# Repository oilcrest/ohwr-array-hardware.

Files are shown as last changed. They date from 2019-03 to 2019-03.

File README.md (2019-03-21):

# Overview

Hardware of the ARRAY system for silicon sensor testing consisting of two Printed Circuit Boards:
* an active 512-to-1 switching matrix,
* a passive probe card to contact the sensor.

# Copyright

Copyright CERN 2013.
This documentation describes Open Hardware and is licensed under the CERN OHL v. 1.2.

You may redistribute and modify this documentation under the terms of the CERN OHL v.1.2. (http://ohwr.org/cernohl). This documentation is distributed WITHOUT ANY EXPRESS OR IMPLIED WARRANTY, INCLUDING OF MERCHANTABILITY, SATISFACTORY QUALITY AND FITNESS FOR A PARTICULAR PURPOSE. Please see the CERN OHL v.1.2 for applicable conditions.

# PCB design files

* [Switching matrix design](/Switching_Matrix)
* [Probe card design](/Probe_Card)

# PCB images

Switching matrix

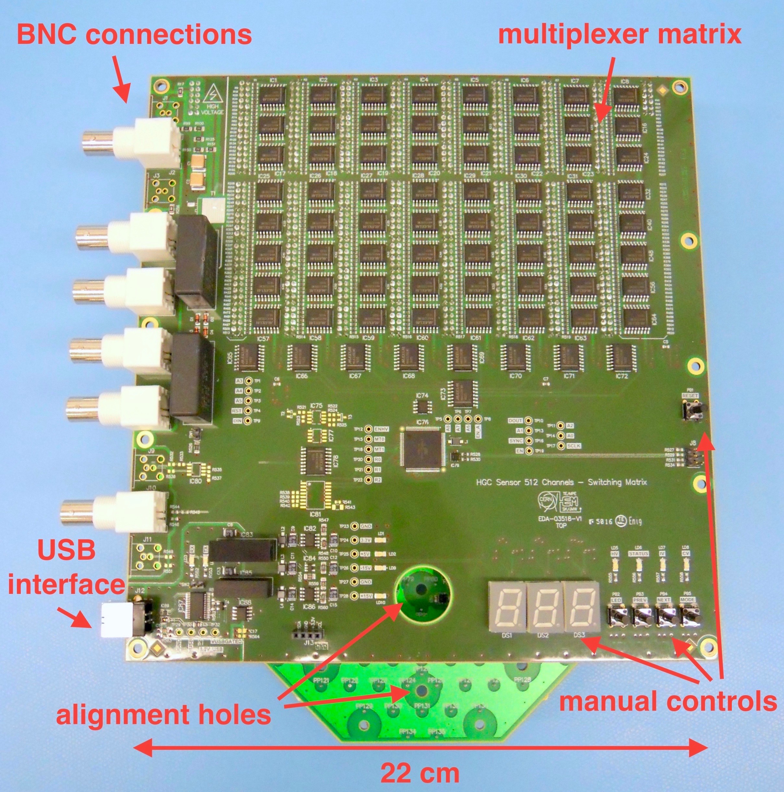
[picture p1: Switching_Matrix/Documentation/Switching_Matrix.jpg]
SwitchingMatrix


Probe card

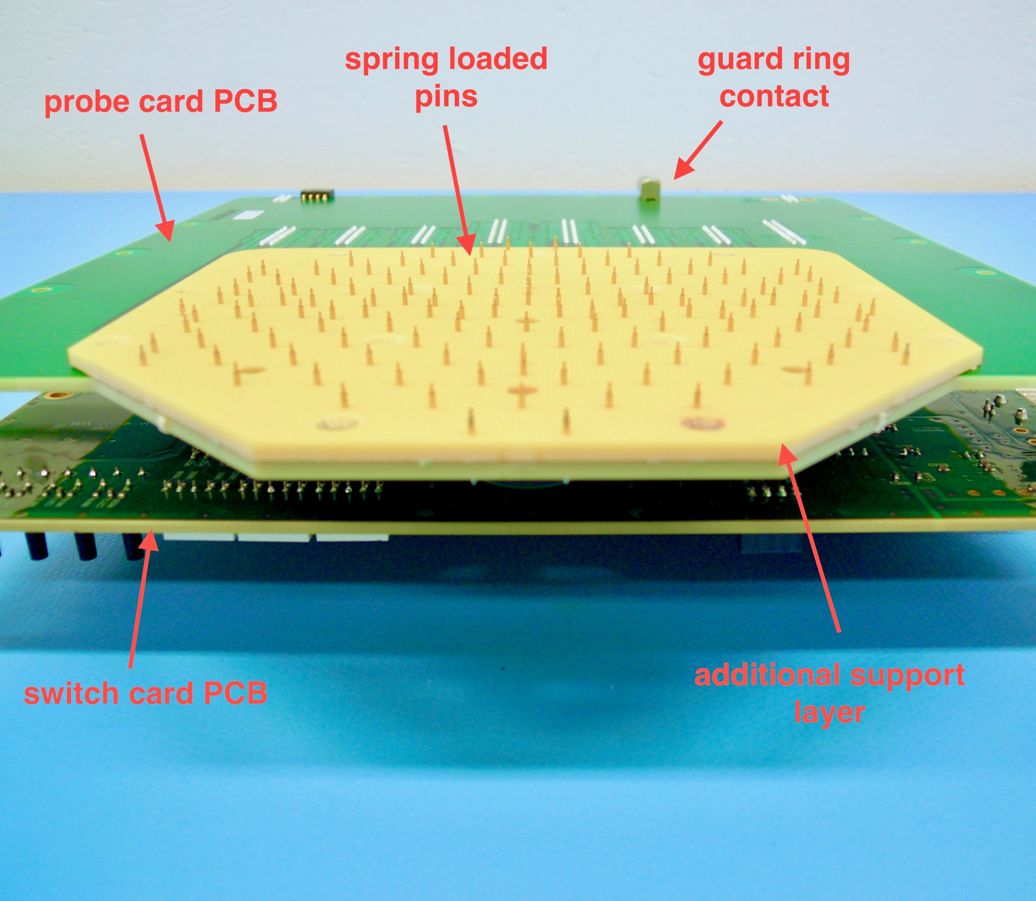
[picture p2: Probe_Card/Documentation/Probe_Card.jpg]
ProbeCard


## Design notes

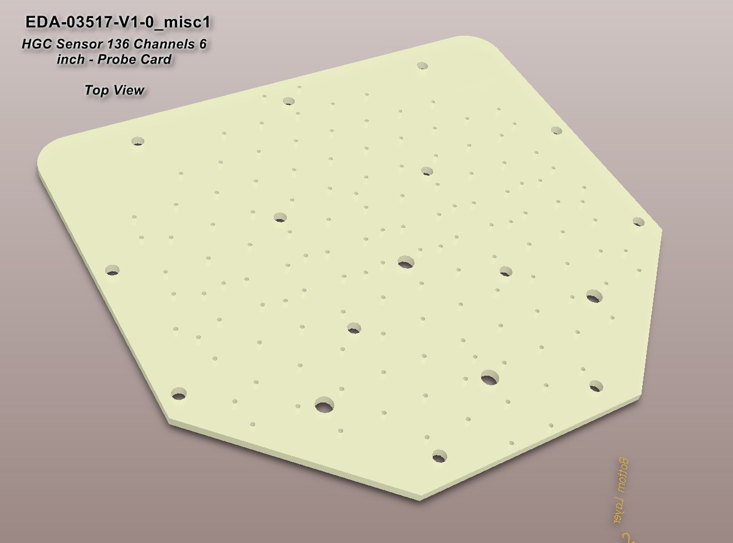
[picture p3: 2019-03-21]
Probe_Card/Picture/EDA-03517-V1-0_3D_misc1-top.jpg

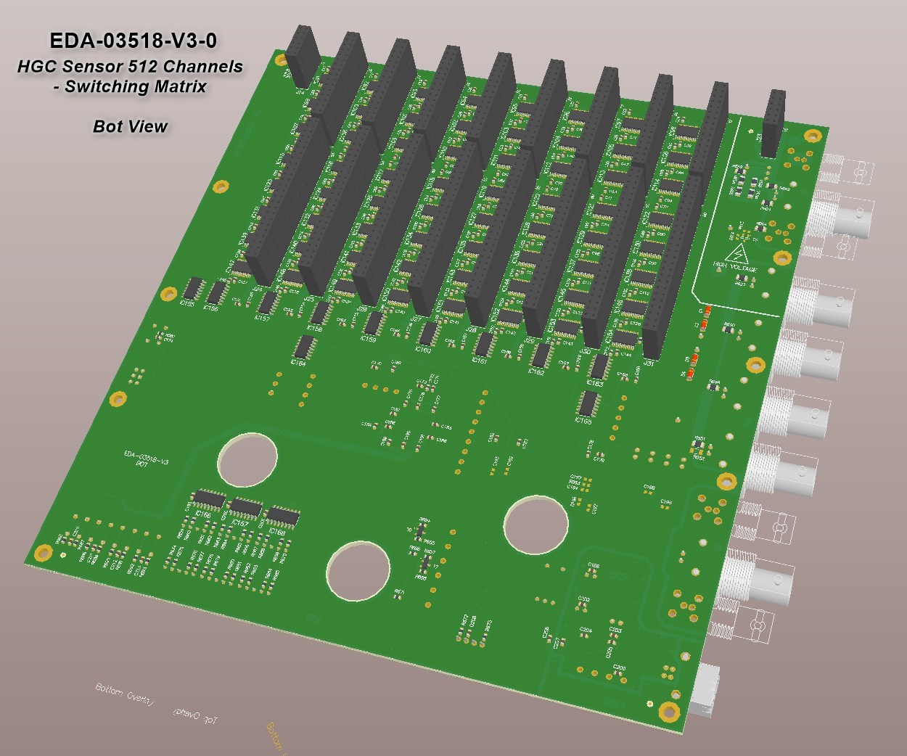
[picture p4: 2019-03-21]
Switching_Matrix/Picture/EDA-03518-V3-0_3D-bot.jpg

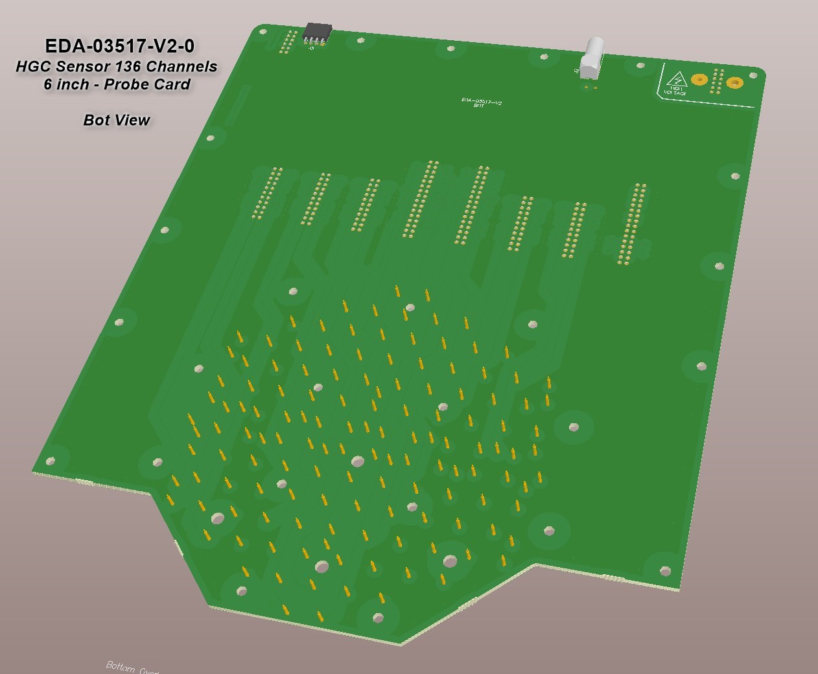
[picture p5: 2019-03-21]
Probe_Card/Picture/EDA-03517-V2-0_3D-bot.jpg

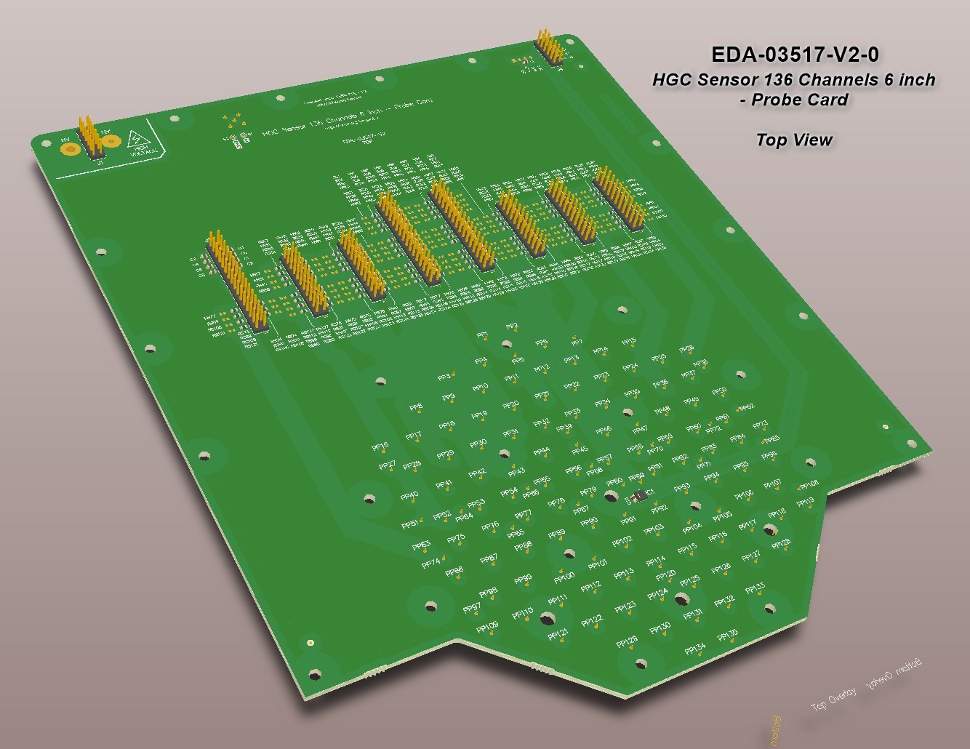
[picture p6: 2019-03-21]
Probe_Card/Picture/EDA-03517-V2-0_3D-top.jpg

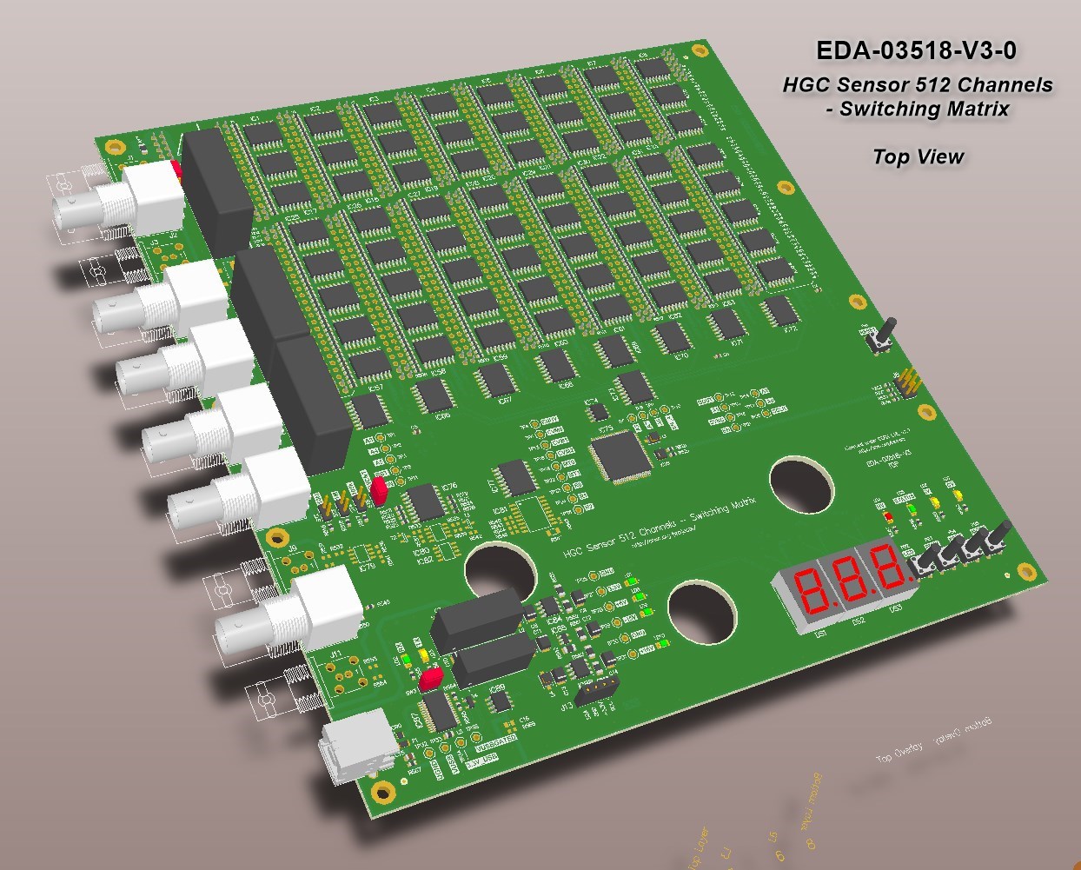
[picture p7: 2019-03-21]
Switching_Matrix/Picture/EDA-03518-V3-0_3D-top.jpg

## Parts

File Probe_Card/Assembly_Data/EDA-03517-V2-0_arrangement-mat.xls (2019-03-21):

 |  | Project | -
 |  | Title | HGC Sensor 136 Channels 6 inch - Probe Card
 |  | EDA Number | EDA-03517-V2-0 | Rev.
 |  | Designer | E. Sicking | Drawn by | JMW
 |  | File | EDA-03517-V2-0_arrangement-mat.xls | EDMS Link | https://edms.cern.ch/nav/EDA-03517-V2-0 | https://edms.cern.ch/nav/EDA-03517-V2-0
 |  | Date | 2019-02-12
Ref | Qty | Scem | Description | Val&Device | Manufacturer | Part Number | Observations
PCBs
1 | 1 |  | "HGC Sensor 136 Channels 6 inch - Probe Card" Printed Circuit | EDA-03517-V2-0 (https://edms.cern.ch/nav/EDA-03517-V2-0) |  |  | EDA-03517-V2-0_pcb
2 | 1 |  | "HGC Sensor 136 Channels 6 inch - Probe Card_misc1" Printed Circuit | https://edms.cern.ch/nav/EDA-03517-V2-0 |  |  | EDA-03517-V1-0_misc1
Screws
10 | 13 |  | Hexalobular (6 Lobe) Socket Flat Head Countersunk Screw, Fully Threaded, ISO 14581, Stainless Steel A2 | M3 - L=8mm | BOSSARD | BN 3803 Article No. 3061684
11 | 13 |  | Waved Spring Washer, DIN 137 B, Spring Steel 440-520 HV, Zinc Plated Blue | fit for M3 | BOSSARD | BN 83728 Article No. 8243964
12 | 13 |  | Hexagonal Nut ~0.8D, DIN 934, Stainless Steel A2 | M3 | BOSSARD | BN 628 Article No. 1241443

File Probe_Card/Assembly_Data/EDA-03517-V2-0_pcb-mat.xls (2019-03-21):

 |  | Project | -
 |  | Title | HGC Sensor 136 Channels 6 inch Probe Card
 |  | EDA Number | EDA-03517-V2-0 | Rev.
 |  | Designer | E. Sicking | Drawn by | JMW
 |  | File | EDA-03517-V2-0_pcb-mat.xls | EDMS URL | https://edms.cern.ch/item/EDA-03517-V2-0
 |  | Date | 2019-02-20
Ref | Qty | Scem | Description | Val&Device | Manufacturer | Part Number | Case
C1 | 2 |  | ±10% 50V X7R SMD Multilayer Chip Ceramic Capacitor | 100nF | GENERIC | CC0603_100NF_50V_10%_X7R | 0603
C10
C2 | 1 |  | ±0.25pF 50V C0G/NP0 SMD Multilayer Chip Ceramic Capacitor | 1pF | GENERIC | CC0603_1PF_50V_0.25PF_NP0 | 0603
C3 | 1 |  | ±0.25pF 50V C0G/NP0 SMD Multilayer Chip Ceramic Capacitor | 2.2pF | GENERIC | CC0603_2.2PF_50V_0.25PF_NP0 | 0603
C4 | 1 |  | ±0.25pF 50V C0G/NP0 SMD Multilayer Chip Ceramic Capacitor | 4.7pF | GENERIC | CC0603_4.7PF_50V_0.25PF_NP0 | 0603
C5 | 1 |  | ±5% 50V C0G/NP0 SMD Multilayer Chip Ceramic Capacitor | 10pF | GENERIC | CC0603_10PF_50V_5%_NP0 | 0603
C6 | 1 |  | ±5% 50V C0G/NP0 SMD Multilayer Chip Ceramic Capacitor | 22pF | GENERIC | CC0603_22PF_50V_5%_NP0 | 0603
C7 | 1 |  | ±5% 50V C0G/NP0 SMD Multilayer Chip Ceramic Capacitor | 47pF | GENERIC | CC0603_47PF_50V_5%_NP0 | 0603
C8 | 1 |  | ±5% 50V C0G/NP0 SMD Multilayer Chip Ceramic Capacitor | 100pF | GENERIC | CC0603_100PF_50V_5%_NP0 | 0603
C9 | 1 |  | ±5% 50V C0G/NP0 SMD Multilayer Chip Ceramic Capacitor | 220pF | GENERIC | CC0603_220PF_50V_5%_NP0 | 0603
J1 | 2 |  | 12 Contacts, Pitch 2.54mm, Dual Row Through Mount Straight Header |  | SAMTEC | MTLW-106-07-L-D-250
J4 |  |  | (Post Lead = 6.35mm, Tail Lead 3.05mm, Insulator 1.52mm)
J2 | 1 | 09.46.11.180.6 (https://edh.cern.ch/edhcat/Browser?command=searchItems&scem=09.46.11.180.6) | Size 00, 50 Ohms Coaxial Elbow (90°) socket With Clearance Under The Body |  | LEMO | EPK.00.250.NTN
J3 | 1 |  | 4 Contacts, Pitch 2.54mm, Single Row Through Mount Right Angle Socket (Lead Length 2.54mm) |  | SAMTEC | SSW-104-02-L-S-RA
J5 | 3 |  | 32 Contacts, Pitch 2.54mm, Dual Row Through Mount Straight Header |  | SAMTEC | MTLW-116-07-L-D-250
J8, J9 |  |  | (Post Lead = 6.35mm, Tail Lead 3.05mm, Insulator 1.52mm)
J6, J7 | 5 |  | 22 Contacts, Pitch 2.54mm, Dual Row Through Mount Straight Header |  | SAMTEC | MTLW-111-07-L-D-250
J10 > J12 |  |  | (Post Lead = 6.35mm, Tail Lead 3.05mm, Insulator 1.52mm)
PP1 > PP135 | 135 |  | Probe, Spring-Loaded Pin, 2A Continuous, 3A Peak, -55..125°C (Soldered Pin 3.81mm) |  | MILL-MAX | 0985-1-15-20-71-14-11-0
RS1 > RS135 | 135 |  | 1A (0.05R Max DC Resistance) Zero Ohm Jumper | 0 | GENERIC | R0603_0R_JUMPER | 0603
Sensitive
IC1 | 1 |  | I2C Digital Humidity 0 – 100% RH and Temperature -40°C to +125°C Sensor | SHT25 | SENSIRION | SHT25 | SON6
Not Mounted
R1 > R4 | 4 |  | ±1% 0.1W ±100ppm/°C General Purpose Thick Film Chip Resistor | 10k | GENERIC | R0603_10K_1%_0.1W_100PPM | 0603
RB1 > RB135 | 135 |  | ±1% 0.125W ±100ppm/°C High Stability Metal Glaze Thick Film Chip Resistor | 10M | VISHAY SFERNICE | CHP0603K1005FNT | 0603
 | Dimensions: |  | Through Pins | 427
 | 220 x 264mm |  | SMD pins on Top | 297
 |  |  | SMD pins on Bottom | 0
 |  |  | Total number of pins | 724

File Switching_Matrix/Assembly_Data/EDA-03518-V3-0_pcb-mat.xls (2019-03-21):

 |  | Project | HGC Sensor Probe Card
 |  | Title | HGC Sensor 512 Channels - Switching Matrix
 |  | EDA Number | EDA-03518-V3-0 | Rev.
 |  | Designer | Szymon Kulis | Drawn by | JMW
 |  | File | EDA-03518-V3-0_pcb-mat.xls | EDMS URL | https://edms.cern.ch/item/EDA-03518-V3-0
 |  | Date | 2019-02-21
Ref | Qty | Scem | Description | Val&Device | Manufacturer | Part Number | Case
C1 > C3 | 3 |  | ±5% 1200VDC Metallized Polypropylene Film Capacitor (MKP1848C DC-Link) | 1uF | VISHAY ROEDERSTEIN | MKP1848C51012JK2 | LS27.5 W11 x L32 x H21
C4 > C6 | 188 |  | ±10% 50V X7R SMD Multilayer Chip Ceramic Capacitor | 100nF | GENERIC | CC0603_100NF_50V_10%_X7R | 0603
C17 > C171
C173 > C186
C189 > C191
C199 > C201
C203 > C208
C210 > C213
C7 > C14 | 8 |  | ±10% 20V Low ESR 0R4 Solid Tantalum Chip Capacitor | 22uF | GENERIC | CTE3528-21_22UF_20V_10%_LESR0400 | B
C15 | 1 |  | ±10% 250V X7R SMD Multilayer Chip Ceramic Capacitor | 4.7nF | GENERIC | CC0805_4.7NF_250V_10%_X7R | 0805
C172 | 1 |  | ±20% 16V X5R SMD Multilayer Chip Ceramic Capacitor | 10uF | GENERIC | CC0603_10UF_16V_20%_X5R | 0603
C198 | 3 |  | ±10% 50V X7R SMD Multilayer Chip Ceramic Capacitor | 10nF | GENERIC | CC0603_10NF_50V_10%_X7R | 0603
C202
C209
D1 > D4 | 4 |  | 10V 500mW Voltage Regulator Diode | BZV55-B10 | NEXPERIA | BZV55-B10 | SOD-80C
DS1 > DS3 | 3 |  | 13.2mm Single Digit 7-Segment Red Display, Common Anode, Right Hand Dot Point | SA52-11SRWA | KINGBRIGHT | SA52-11SRWA
F1 | 1 |  | PTC Resettable Fuse | 500mA-6V | BOURNS | MF-PSMF050X-2
IC1 > IC73 | 75 |  | Ultra-Low Leakage Monolithic CMOS Analog Multiplexers | MAX328EWE+ | MAXIM | MAX328EWE+ | SOIC16W
IC76, IC77
IC74 | 1 |  | 2.048V Output, ±1mV ±0.05% Accuracy, 3ppm/°C Ultralow Noise XFET Voltage References with Current Sink and Source Capability | ADR440BRZ | ANALOG DEVICES | ADR440BRZ | SOIC8
IC75 | 1 |  | 8/16-bit AVR XMEGA A1U Microcontroller, 1.6-3.6V, 128KB + 8KB Flash, 2KB EEPROM, 8KB SRAM, 100-pin TQFP, Industrial Grade (-40°C to 85°C), Pb-Free | ATXMEGA128A1U-AU | ATMEL | ATXMEGA128A1U-AU | QFP100
IC83 | 1 |  | 5V ±10% to 5V, Iout (max) 200mA, 1W DC-DC Converter | TMV 0505EN | TRACO POWER | TMV 0505EN
IC84 | 2 |  | 20V, 500mA, Low Noise, CMOS LDO Linear Regulator | ADP7104ARDZ-R7 | ANALOG DEVICES | ADP7104ARDZ-R7 | SOIC8
IC88
IC85 | 1 |  | -1.22V to -27V, -200mA, Adjustable, Low Noise, Negative Linear Regulator | ADP7182AUJZ-R7 | ANALOG DEVICES | ADP7182AUJZ-R7 | SOT23-5
IC86 | 1 |  | 5V ±10% to ±15V, Iout (max) ±65mA, 1W DC-DC Converter | TMV 0515D | TRACO POWER | TMV 0515D
IC87 | 1 |  | USB to serial UART Interface | FT232RL | FUTURE TECHNOLOGYDEVICES INTERNATIONAL (FTDI) | FT232RL | SSOP28
IC89 | 1 |  | Dual Channel Digital Isolator | ISO7221AD | TEXAS INSTRUMENTS | ISO7221AD | SOIC8
IC90 | 1 |  | 2 Data-Line Protection, Very Low Capacitance ESD Protection | USBLC6-2P6 | ST MICROELECTRONICS | USBLC6-2P6 | SOT666
IC91 > IC154 | 64 |  | 9.5 Ohm ON Resistance, ±15 V/+12 V/±5 V iCMOS, Serially-Controlled Octal SPST Switches | ADG1414BRUZ | ANALOG DEVICES | ADG1414BRUZ | TSSOP24
IC155 > IC165 | 11 |  | Hex Inverters | 74HC04D | NXP SEMICONDUCTORS | 74HC04D | SOIC14
IC166 > IC168 | 3 |  | 8-Bit Shift Register With 3-State Output Registers | SN74HC595D | TEXAS INSTRUMENTS | SN74HC595D | SOIC16
J2 | 6 |  | 50 Ohms BNC Elbow PCB Socket With Mounting Posts |  | TYCO ELECTRONICS | 1-1337543-0
J4 > J7
J10
J8 | 1 |  | 6 Contacts, Pitch 2.54mm, Dual Row Through Mount Straight Header (Post Lead = 6.35mm, Tail Lead 3.05mm, Insulator 1.52mm) |  | SAMTEC | MTLW-103-07-L-D-250
J12 | 1 |  | Thru Hole, Right Angle, 4 Position, Type B, USB Receptacle |  | TYCO ELECTRONICS | 292304-1
J13 | 1 |  | 4 Contacts, Pitch 2.54mm, Single Row Through Mount Straight Socket (Lead Length 4.93mm) |  | SAMTEC | SSW-104-02-L-S
J14 | 2 |  | 12 Contacts, Pitch 2.54mm, Dual Row Through Mount Straight Elevated Socket, |  | SAMTEC | ESW-106-69-L-D
J23 |  |  | Low Insertion Force (Lead Length 4.57mm)
J15 > J22 | 8 |  | 32 Contacts, Pitch 2.54mm, Dual Row Through Mount Straight Elevated Socket, Low Insertion Force (Lead Length 4.57mm) |  | SAMTEC | ESW-116-69-L-D
J24 > J31 | 8 |  | 50 Contacts, Pitch 2.54mm, Dual Row Through Mount Straight Elevated Socket, Low Insertion Force (Lead Length 4.57mm) |  | SAMTEC | ESW-125-69-L-D
L1 | 1 |  | ±10% 450mA Chip Inductor (Chip Coil) for Choke Wire Wound Type | 10uH | MURATA | LQH32CN100K33L
L2 > L4 | 3 |  | ±20% 650mA Chip Inductor (Chip Coil) for Choke Wire Wound Type | 4.7uH | MURATA | LQH32CN4R7M33L
L5 | 1 |  | ±25% 2A SMD EMI Suppression Chip Ferrite Bead (WE-CBF Series) | 330R@100MHz | WURTH ELEKTRONIK | 742792037 | 0805
LD1, LD2 | 6 |  | Surface Mount Green LED (1206 Case) |  | AVAGO TECHNOLOGIES | HSMG-C150 | 1206
LD5
LD8 > LD10
LD3 | 3 |  | Yellow Diffused Surface Mount LED (1206 Case) |  | AVAGO TECHNOLOGIES | HSMY-C150 | 1206
LD6, LD7
LD4 | 1 |  | Surface Mount Red LED (1206 Case) |  | AVAGO TECHNOLOGIES | HSMC-C150 | 1206
R1 > R16 | 525 |  | ±1% 0.1W ±100ppm/°C General Purpose Thick Film Chip Resistor | 10k | GENERIC | R0603_10K_1%_0.1W_100PPM | 0603
R18 > R249
R251 > R514
R526
R529
R569, R570
R579, R580
R650
R672, R673
R686
R688
R690
R692
R17 | 10 |  | 2A (0.05R Max DC Resistance) Zero Ohm Jumper | 0 | GENERIC | R1206_0R_JUMPER | 1206
R250
R589
R592
R603, R604
R623
R640
R649
R651
R515 | 2 |  | ±1% 0.1W ±100ppm/°C General Purpose Thick Film Chip Resistor | 10M | GENERIC | R0603_10M_1%_0.1W_100PPM | 0603
R521
R516 | 2 |  | ±1% 0.1W ±100ppm/°C General Purpose Thick Film Chip Resistor | 1M | GENERIC | R0603_1M_1%_0.1W_100PPM | 0603
R522
R517, R518 | 9 |  | ±1% 0.1W ±100ppm/°C General Purpose Thick Film Chip Resistor | 100k | GENERIC | R0603_100K_1%_0.1W_100PPM | 0603
R565
R654
R657
R687
R689
R691
R693
R519 | 1 |  | ±1% 0.1W ±100ppm/°C High-Value High-voltage (150V) Wraparound Chip Resistor | 5M | OHMITE | HVC0603T5004FET | 0603
R520 | 1 |  | ±1% 0.1W ±100ppm/°C General Purpose Thick Film Chip Resistor | 510k | GENERIC | R0603_510K_1%_0.1W_100PPM | 0603
R523 | 6 |  | 1A (0.05R Max DC Resistance) Zero Ohm Jumper | 0 | GENERIC | R0603_0R_JUMPER | 0603
R527
R530
R534
R548
R550
R524 | 1 |  | ±5% 0.1W ±100ppm/°C High-Value High-voltage (150V) Wraparound Chip Resistor | 50M | OHMITE | HVC0603T5005FET | 0603
R525 | 1 |  | ±1% 0.1W ±100ppm/°C General Purpose Thick Film Chip Resistor | 2M | GENERIC | R0603_2M_1%_0.1W_100PPM | 0603
R528 | 1 |  | ±1% 0.1W ±100ppm/°C Precision High-Value High-Voltage Wraparound Chip Resistor | 100M | OHMITE | HVC0603T1006FET | 0603
R549 | 1 |  | ±1% 0.1W ±100ppm/°C General Purpose Thick Film Chip Resistor | 51 | GENERIC | R0603_51R_1%_0.1W_100PPM | 0603
R551 | 1 |  | ±1% 0.25W ±100ppm/°C General Purpose Thick Film Chip Resistor | 36k | GENERIC | R1206_36K_1%_0.25W_100PPM | 1206
R552 | 1 |  | ±1% 0.25W ±100ppm/°C General Purpose Thick Film Chip Resistor | 62k | GENERIC | R1206_62K_1%_0.25W_100PPM | 1206
R555, R556 | 2 |  | ±1% 0.1W ±100ppm/°C General Purpose Thick Film Chip Resistor | 220 | GENERIC | R0603_220R_1%_0.1W_100PPM | 0603
R557 > R560 | 5 |  | ±1% 0.1W ±100ppm/°C General Purpose Thick Film Chip Resistor | 330 | GENERIC | R0603_330R_1%_0.1W_100PPM | 0603
R655
R561 | 2 |  | ±1% 0.25W ±100ppm/°C General Purpose Thick Film Chip Resistor | 91k | GENERIC | R1206_91K_1%_0.25W_100PPM | 1206
R566
R562, R563 | 2 |  | ±1% 0.25W ±100ppm/°C General Purpose Thick Film Chip Resistor | 8k2 | GENERIC | R1206_8K2_1%_0.25W_100PPM | 1206
R564 | 1 |  | ±1% 0.1W ±100ppm/°C General Purpose Thick Film Chip Resistor | 1k | GENERIC | R0603_1K_1%_0.1W_100PPM | 0603
R567 | 1 |  | ±1% 0.1W ±100ppm/°C General Purpose Thick Film Chip Resistor | 1M1 | GENERIC | R0603_1M1_1%_0.1W_100PPM | 0603
R571 > R578 | 64 |  | ±1% 0.1W ±100ppm/°C General Purpose Thick Film Chip Resistor | 33k | GENERIC | R0603_33K_1%_0.1W_100PPM | 0603
R581 > R588
R595 > R602
R605 > R612
R615 > R622
R624 > R639
R641 > R648
R590, R591 | 4 |  | ±1% 0.25W ±100ppm/°C General Purpose Thick Film Chip Resistor | 10k | GENERIC | R1206_10K_1%_0.25W_100PPM | 1206
R593, R594
R656 | 1 |  | ±1% 0.1W ±100ppm/°C General Purpose Thick Film Chip Resistor | 750 | GENERIC | R0603_750R_1%_0.1W_100PPM | 0603
R658 | 2 |  | ±1% 0.1W ±100ppm/°C General Purpose Thick Film Chip Resistor | 2k4 | GENERIC | R0603_2K4_1%_0.1W_100PPM | 0603
R671
R659 > R670 | 24 |  | ±1% 0.1W ±100ppm/°C General Purpose Thick Film Chip Resistor | 3k3 | GENERIC | R0603_3K3_1%_0.1W_100PPM | 0603
R674 > R685
ST1 | 1 |  | 3 Contacts, Pitch 2.54mm, Single Row Through Mount Straight Header (Post Lead = 6.35mm, Tail Lead 3.05mm, Insulator 1.52mm) |  | SAMTEC | MTLW-103-07-L-S-250
ST2 > ST6 | 5 |  | 2 Contacts, Pitch 2.54mm, Single Row Through Mount Straight Header (Post Lead = 6.35mm, Tail Lead 3.05mm, Insulator 1.52mm) |  | SAMTEC | MTLW-102-07-L-S-250
SW1 > SW3 | 3 | 09.55.10.950.1 (https://edh.cern.ch/edhcat/Browser?command=searchItems&scem=09.55.10.950.1) | Closed Insulated Red Jumper Pitch 2.54mm |  | STELVIO-KONTEK | 3131730000402
T4 | 1 |  | -20V -3.7A P-Channel HEXFET® Power MOSFET | IRLML6402PBF | INTERNATIONAL RECTIFIER | IRLML6402PBF | SOT23-3
T6 | 1 |  | 60V 280mA N-Channel Enhancement Mode Field Effect Transistor (FET) | 2N7002 | FAIRCHILD SEMICONDUCTOR | 2N7002 | SOT23-3
T7 | 1 |  | -30V -470mA P-Channel Enhancement Mode MOS Transistor | BSH203 | NXP SEMICONDUCTORS | BSH203 | SOT23-3
Sensitive
IC78 | 1 |  | I2C Digital Humidity 0 – 100% RH and Temperature -40°C to +125°C Sensor | SHT25 | SENSIRION | SHT25 | SON6
PB1 > PB5 | 5 |  | 12VDC 50mA, 6x6mm Model, 13mm Stem Height Vertical Pushbutton Switch, ALPS SKHH Series |  | ALPS | SKHHDTA010
Not Mounted
C16 | 1 |  | ±10% 250V X7R SMD Multilayer Chip Ceramic Capacitor | 4.7nF | GENERIC | CC0805_4.7NF_250V_10%_X7R | 0805
C187, C188 | 8 |  | ±10% 50V X7R SMD Multilayer Chip Ceramic Capacitor | 100nF | GENERIC | CC0603_100NF_50V_10%_X7R | 0603
C192 > C197
IC79, IC80 | 2 |  | Dual Low-Noise JFET-Input Operational Amplifier | TL072CD | TEXAS INSTRUMENTS | TL072CD | SOIC8
IC81 | 1 |  | Ultra-Low Leakage Monolithic CMOS Analog Multiplexers | MAX328EWE+ | MAXIM | MAX328EWE+ | SOIC16W
IC82 | 1 |  | Low Power, Low Noise Precision FET Operational Amplifier | AD795JRZ | ANALOG DEVICES | AD795JRZ | SOIC8
J1 | 4 |  | TRB ( Twinax/Triax 500MHz) Right Angle PCB Jack |  | TROMPETER/CINCH | CBBJR79A
J3
J9
J11
R531 | 6 |  | 1A (0.05R Max DC Resistance) Zero Ohm Jumper | 0 | GENERIC | R0603_0R_JUMPER | 0603
R536
R538
R541
R553, R554
R532 | 1 |  | ±1% 0.1W ±100ppm/°C General Purpose Thick Film Chip Resistor | 470 | GENERIC | R0603_470R_1%_0.1W_100PPM | 0603
R533 | 2 |  | ±1% 0.1W ±100ppm/°C General Purpose Thick Film Chip Resistor | 100 | GENERIC | R0603_100R_1%_0.1W_100PPM | 0603
R535
R537 | 5 |  | ±1% 0.1W ±100ppm/°C General Purpose Thick Film Chip Resistor | 10k | GENERIC | R0603_10K_1%_0.1W_100PPM | 0603
R539, R540
R542
R653
R543 | 3 |  | ±1% 0.1W ±100ppm/°C General Purpose Thick Film Chip Resistor | 100k | GENERIC | R0603_100K_1%_0.1W_100PPM | 0603
R613, R614
R544 | 1 |  | ±1% 0.1W ±100ppm/°C General Purpose Thick Film Chip Resistor | 1M | GENERIC | R0603_1M_1%_0.1W_100PPM | 0603
R545 | 1 |  | ±1% 0.1W ±100ppm/°C Precision High-Value High-Voltage Wraparound Chip Resistor | 100M | OHMITE | HVC0603T1006FET | 0603
R546 | 1 |  | ±1% 0.1W ±100ppm/°C General Purpose Thick Film Chip Resistor | 10M | GENERIC | R0603_10M_1%_0.1W_100PPM | 0603
R547 | 1 |  | ±1% 0.3W ±100ppm/°C Thick Film Chip Resistor, High Voltage | 1G | VISHAY TECHNO | CRHV1206AF1G00FKFT | 1206
R568 | 1 |  | ±1% 0.1W ±100ppm/°C General Purpose Thick Film Chip Resistor | 1M1 | GENERIC | R0603_1M1_1%_0.1W_100PPM | 0603
R652 | 1 |  | 2A (0.05R Max DC Resistance) Zero Ohm Jumper | 0 | GENERIC | R1206_0R_JUMPER | 1206
T1 | 1 |  | 1500V 2A N-Channel Power MOSFET | 2SK4177-DL-1E | ON SEMICONDUCTOR | 2SK4177-DL-1E | TO-263-2L
T2, T3 | 3 |  | 60V 280mA N-Channel Enhancement Mode Field Effect Transistor (FET) | 2N7002 | FAIRCHILD SEMICONDUCTOR | 2N7002 | SOT23-3
T5
TP1 > TP35 | 35 |  | Black Bead PCB Terminal Test Pin for 1.6mm PCB Thickness (1.32mm Hole) |  | VERO TECHNOLOGIES | 20-2136
 | Dimensions: |  | Through Pins | 811
 | 220 x 230mm |  | SMD pins on Top | 2548
 |  |  | SMD pins on Bottom | 2372
 |  |  | Total number of pins | 5731

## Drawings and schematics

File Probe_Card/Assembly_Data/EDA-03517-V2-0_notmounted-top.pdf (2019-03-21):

J1 | J4

# 4 Not Mounted TOP

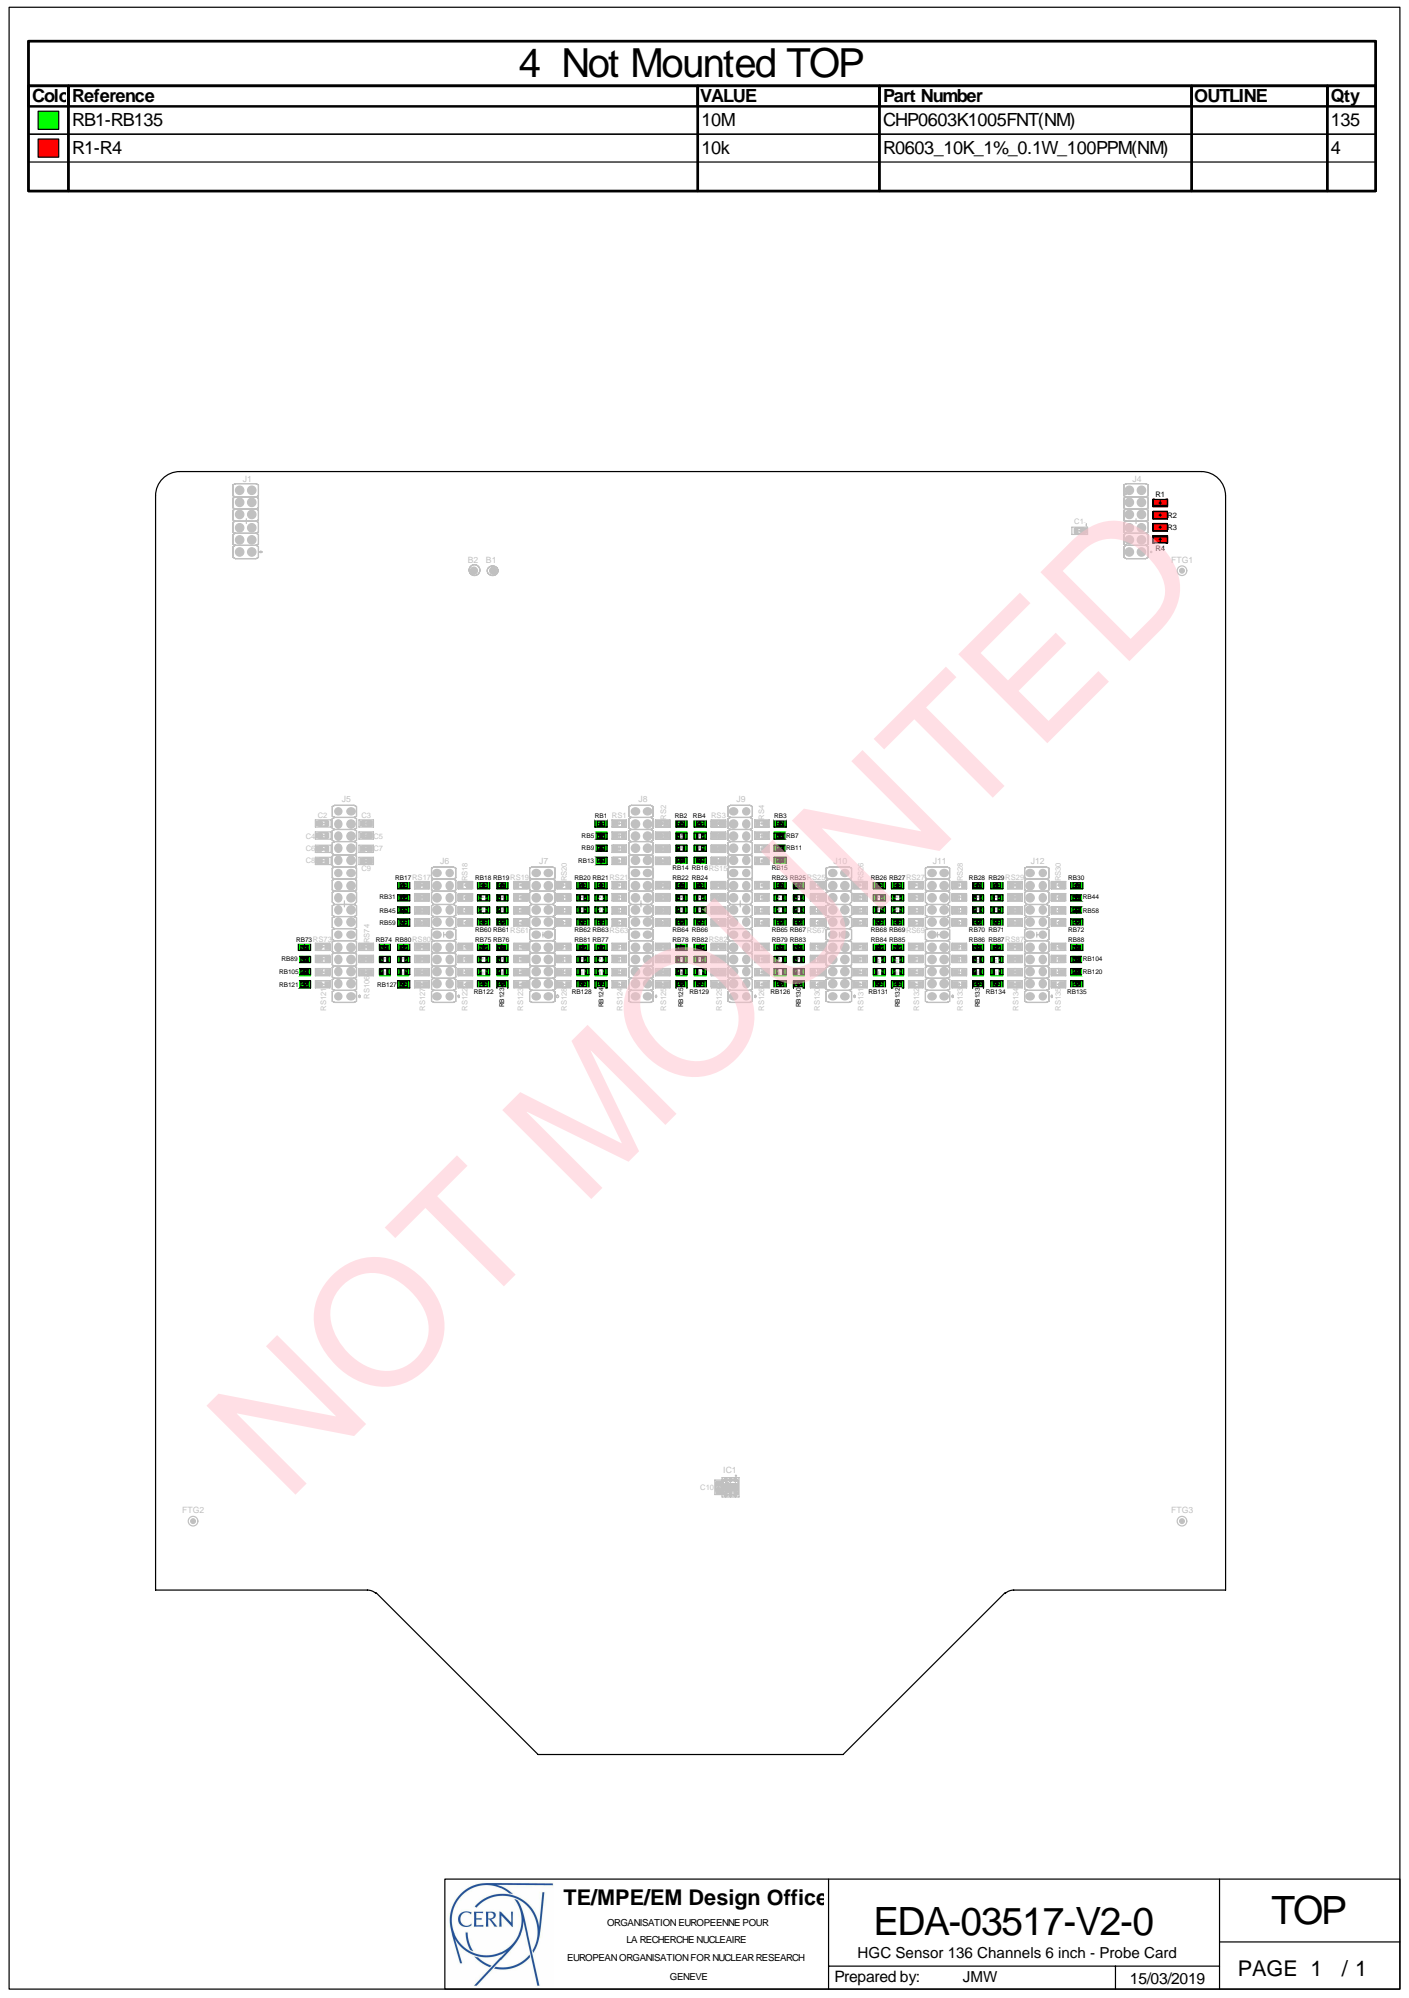
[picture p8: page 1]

TOP TE/MPE/EM Design Office

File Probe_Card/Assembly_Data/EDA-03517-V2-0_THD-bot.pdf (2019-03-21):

J3

# 3 Through-Holes BOTTOM

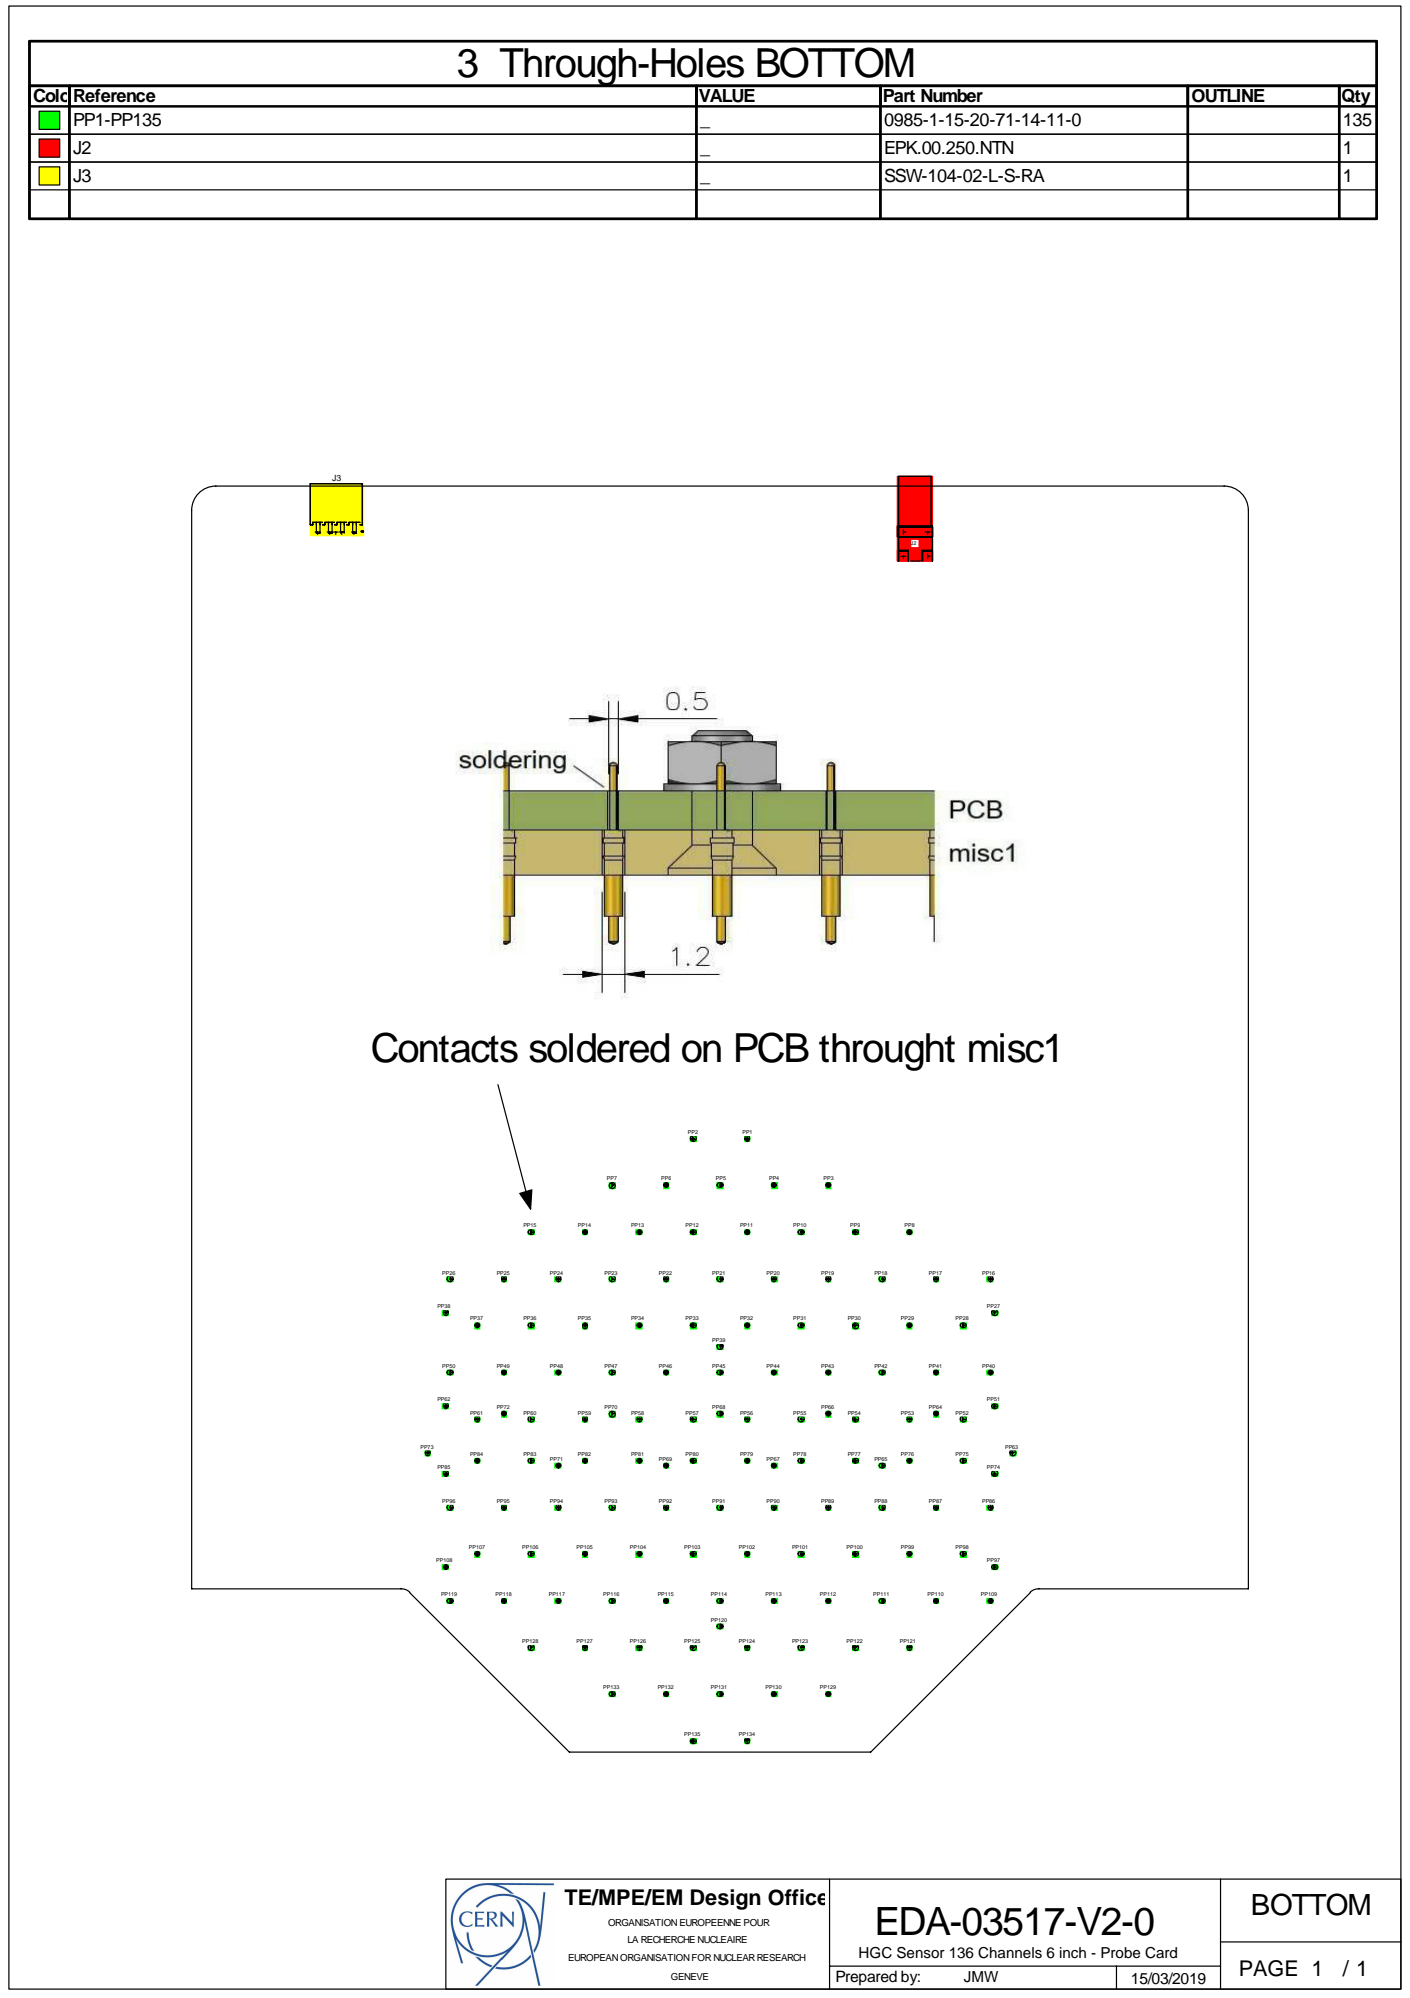
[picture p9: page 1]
EDA-03517-V2-0; TE/MPE/EM Design Office; BOTTOM; GENEVE; EUROPEAN ORGANISATION FOR NUCLEAR RESEARCH; HGC Sensor 136 Channels 6 inch - Probe Card; Prepared by:; JMW

ColorReference | VALUE | Part Number | OUTLINE | Qty
PP1-PP135 | _ | 0985-1-15-20-71-14-11-0 | 135
J2 | _ | EPK.00.250.NTN | 1
J3 | _ | SSW-104-02-L-S-RA | 1

Contacts soldered on PCB throught misc1

ORGANISATION EUROPEENNE POUR
LA RECHERCHE NUCLEAIRE

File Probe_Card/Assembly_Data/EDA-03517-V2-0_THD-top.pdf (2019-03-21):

J1 | J4

# 2 Through-Holes TOP

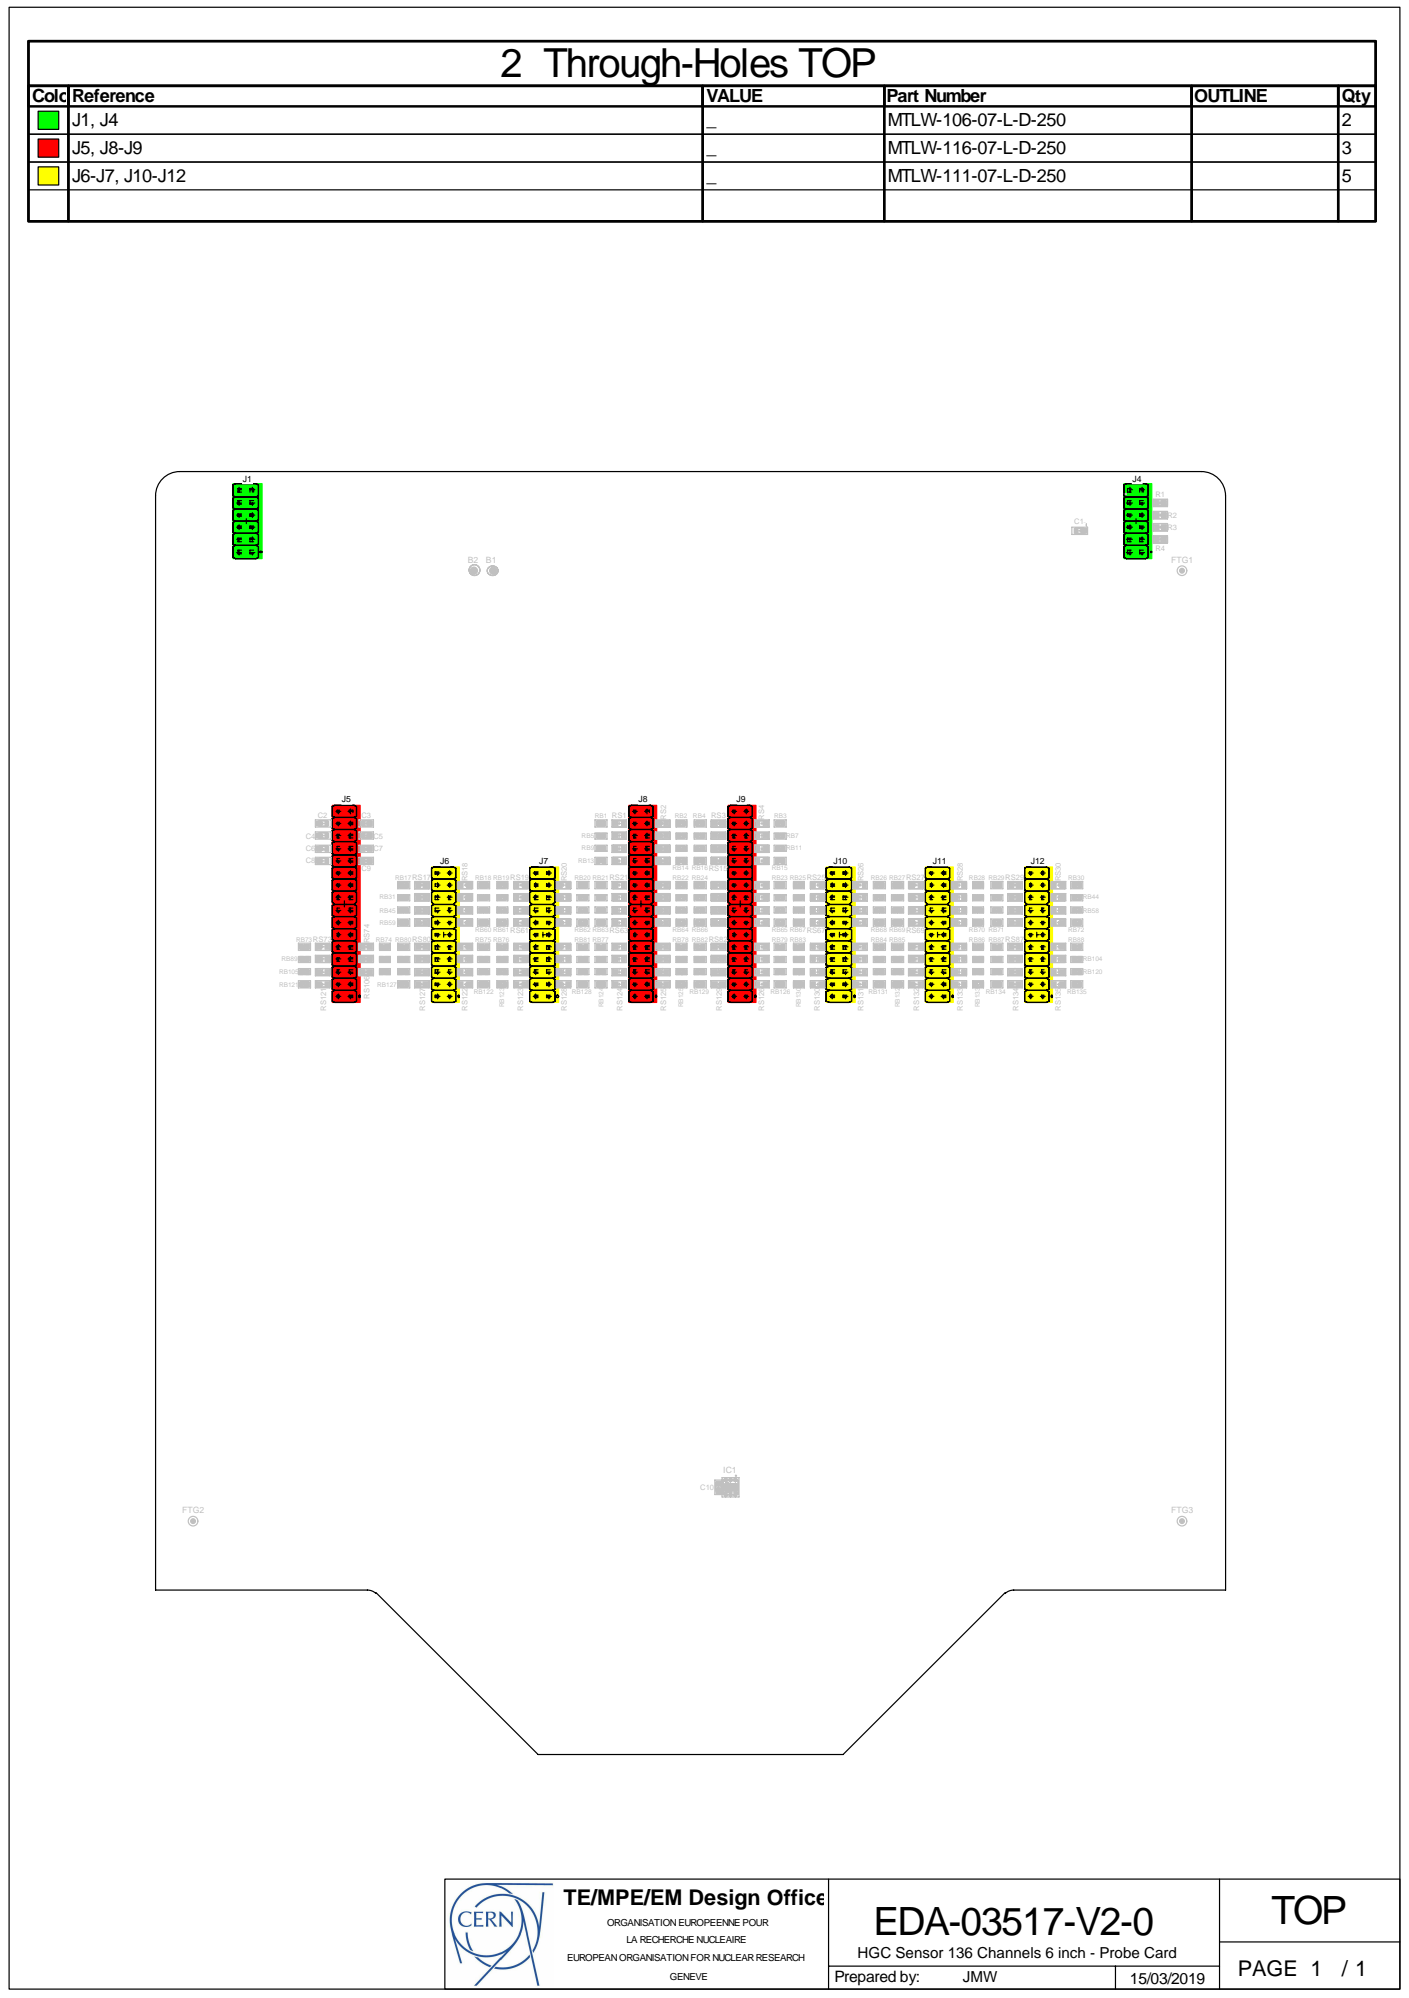
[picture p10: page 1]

TOP TE/MPE/EM Design Office

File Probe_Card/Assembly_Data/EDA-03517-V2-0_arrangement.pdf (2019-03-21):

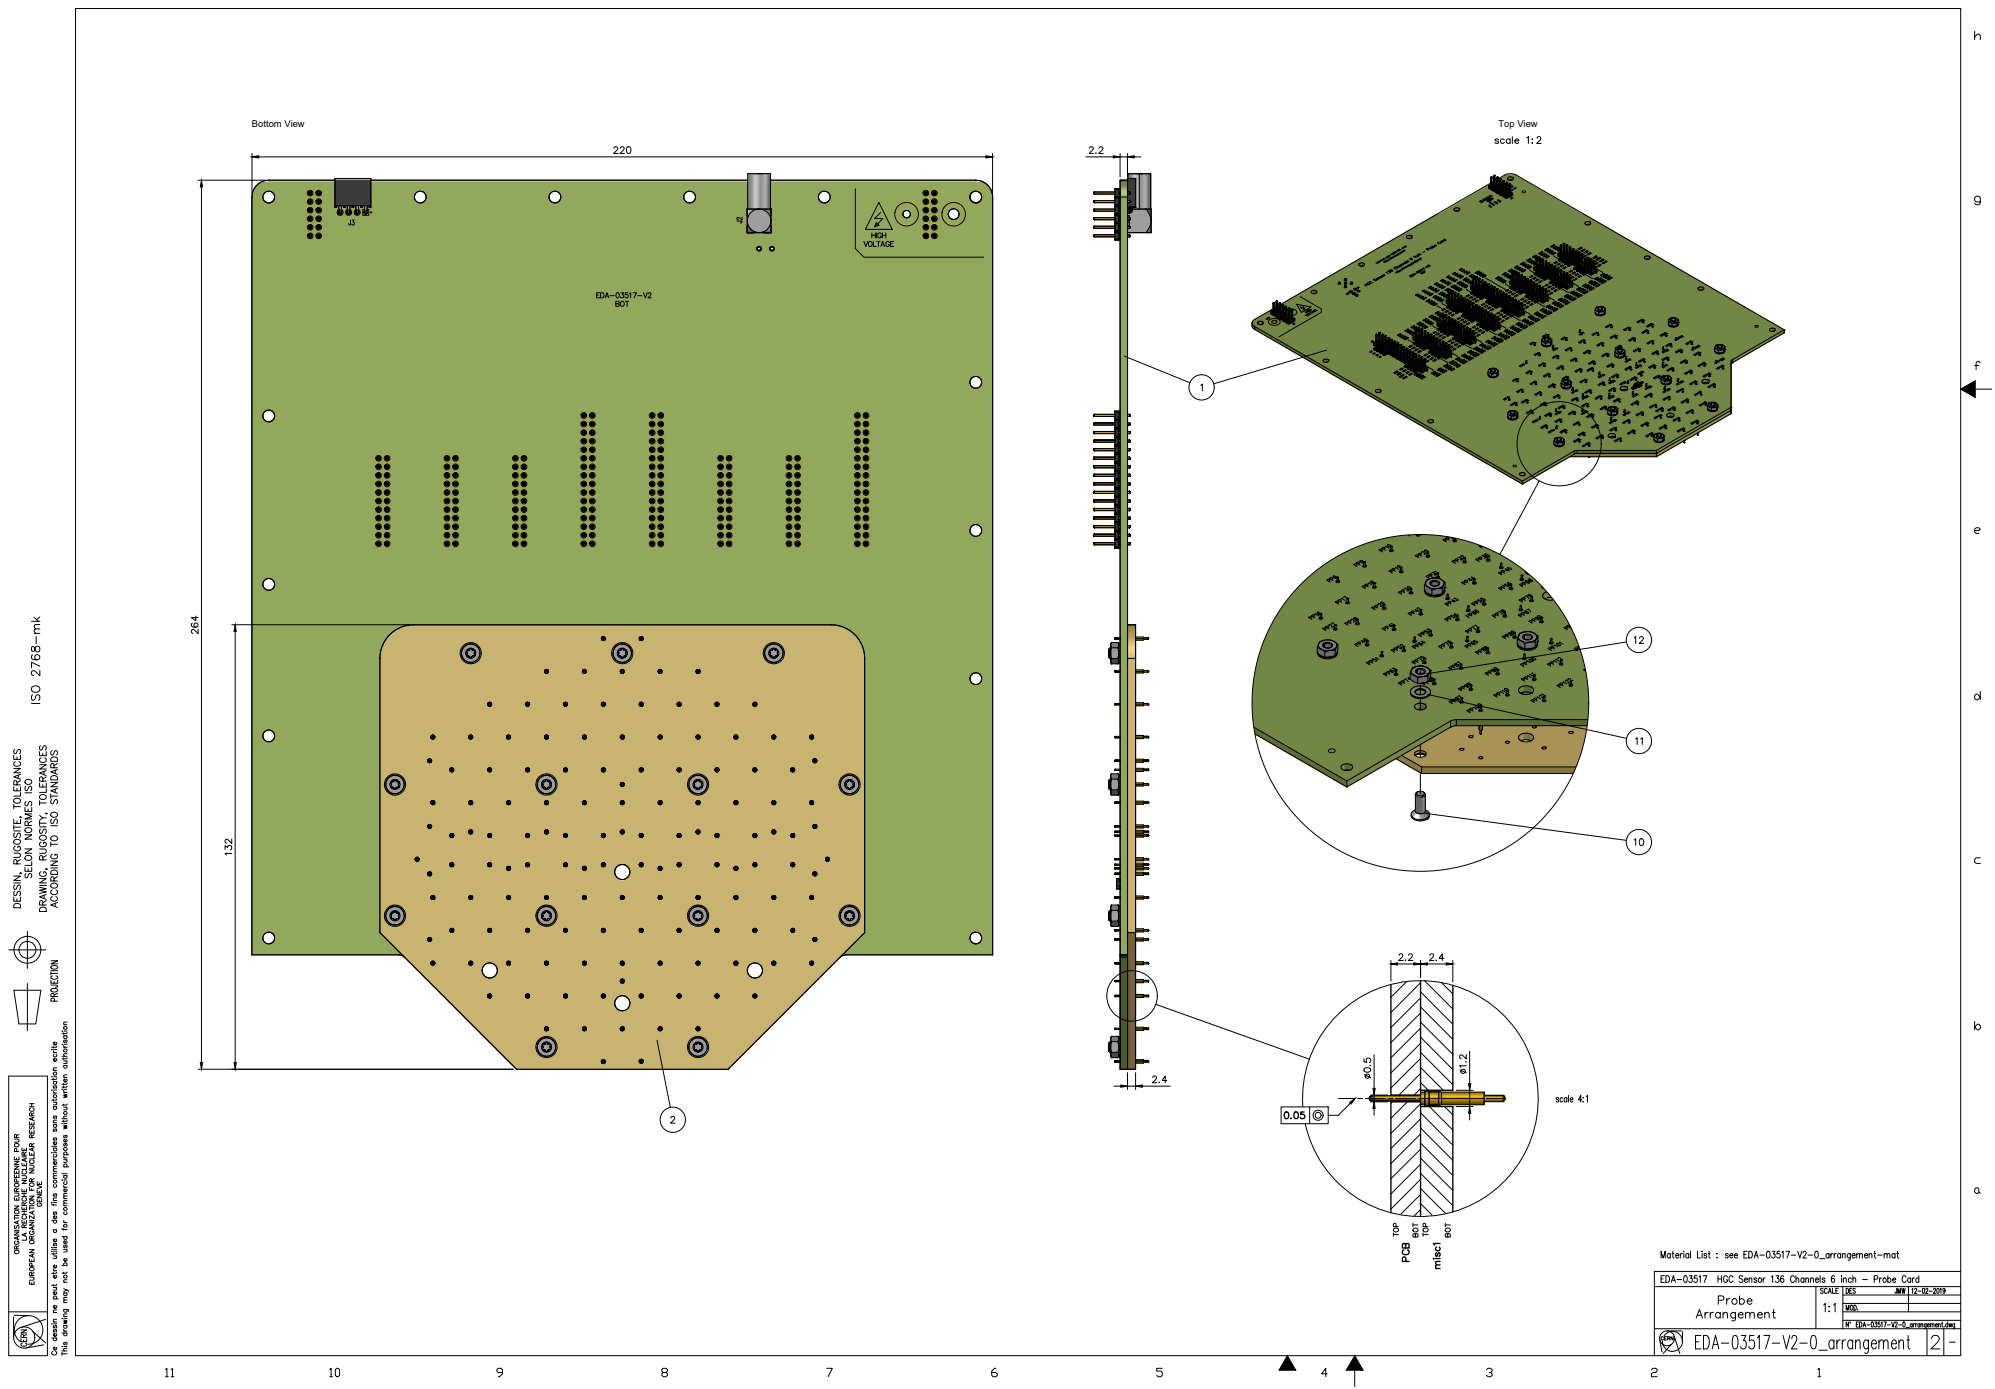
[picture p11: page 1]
Bottom View; Top View

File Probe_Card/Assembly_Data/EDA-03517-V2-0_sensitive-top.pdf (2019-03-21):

J1 | J4

# 5 Sensitive TOP

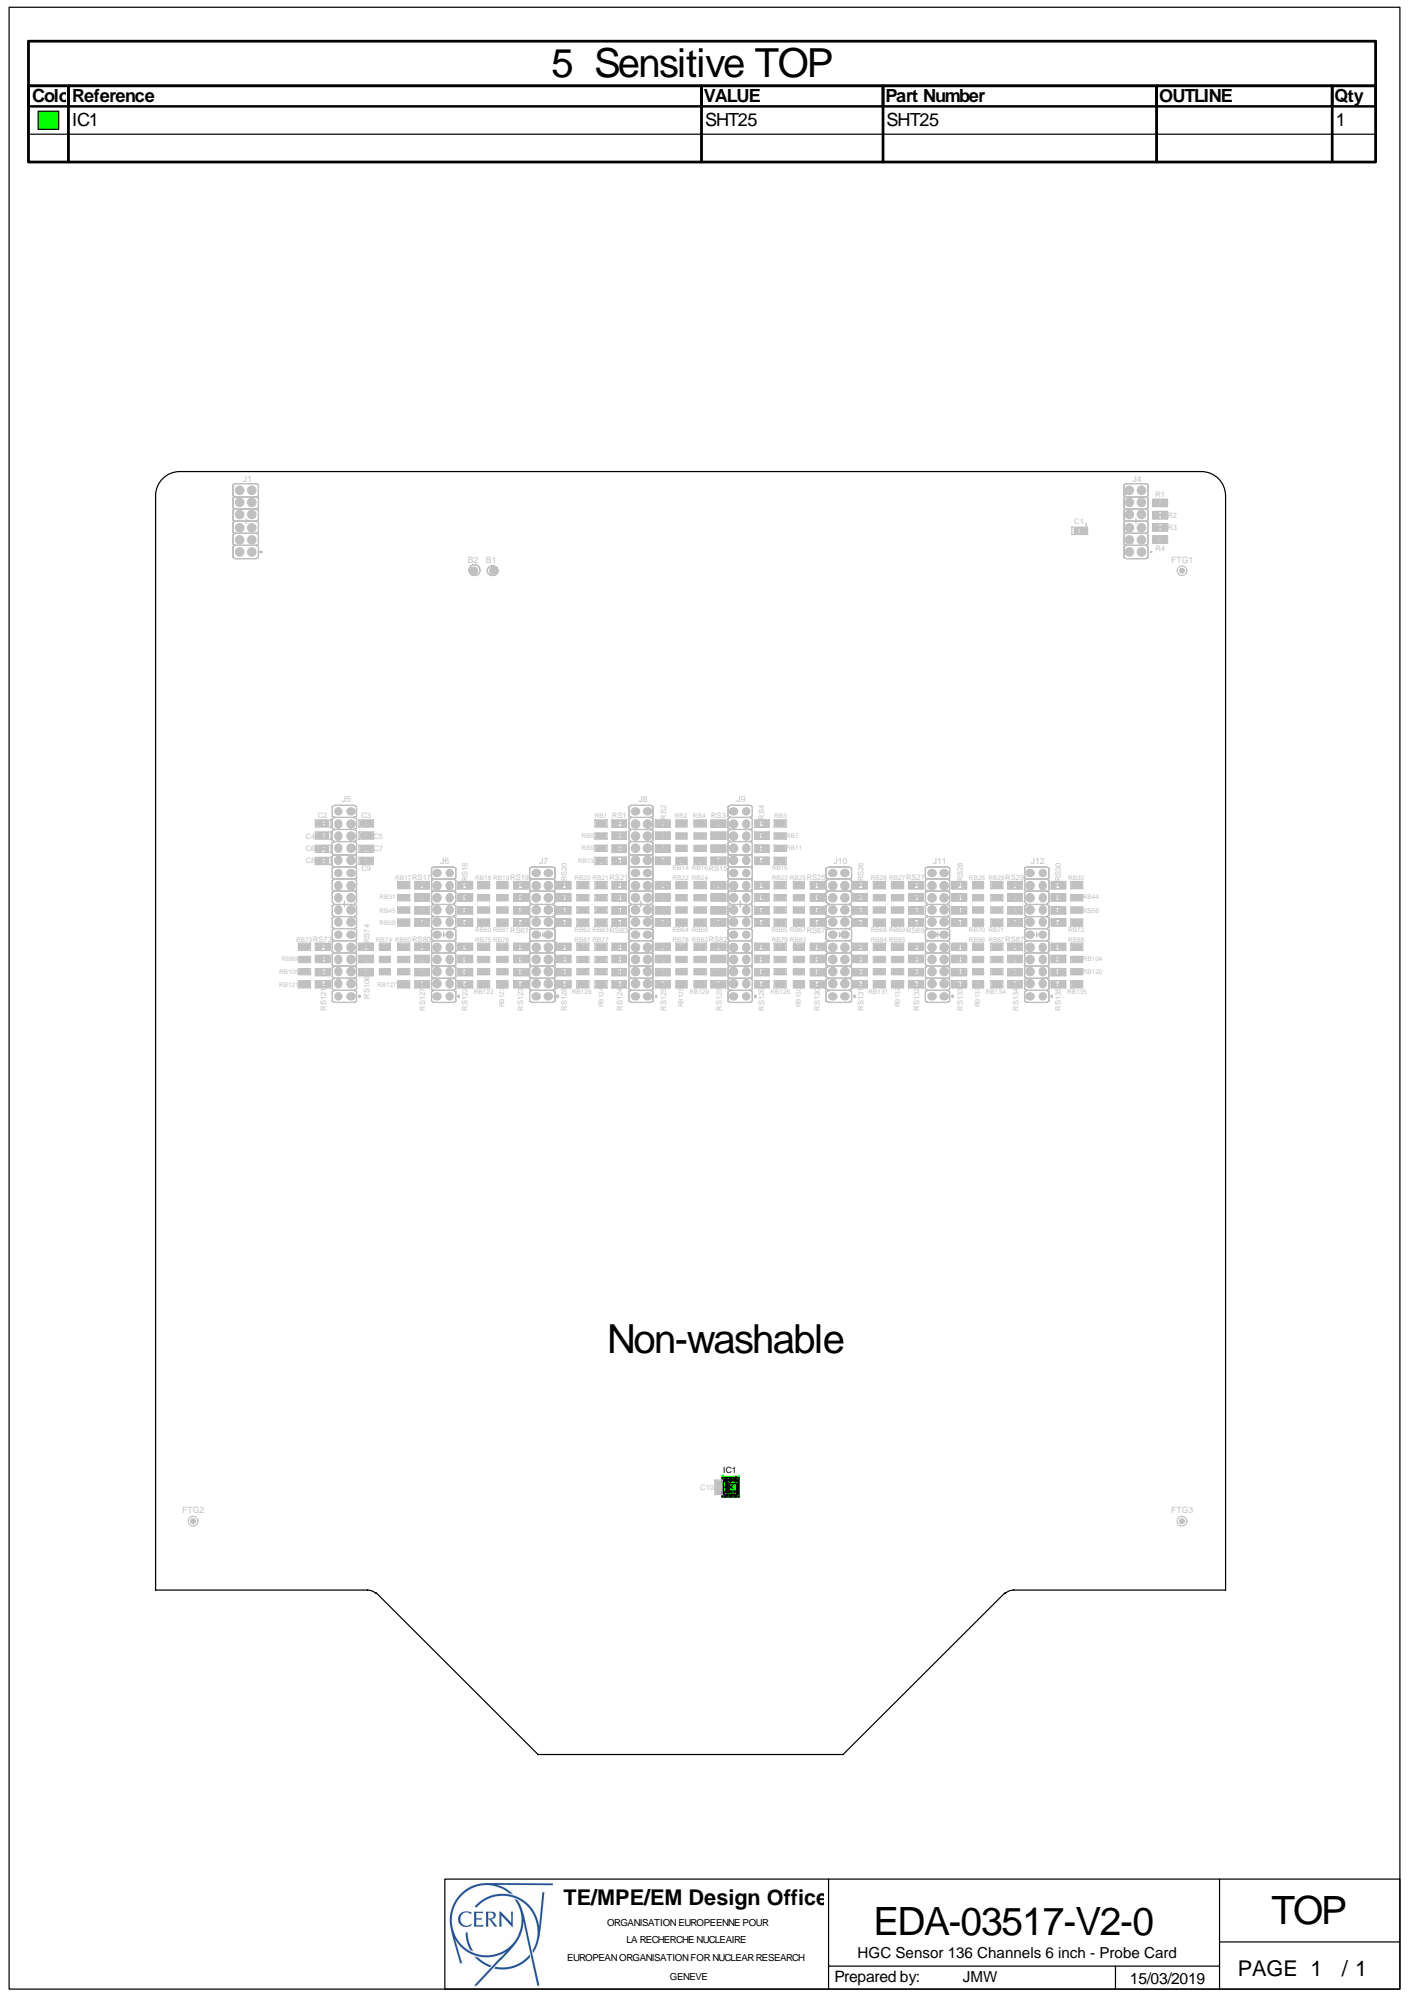
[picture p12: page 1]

ColorReference | VALUE | Part Number | OUTLINE | Qty
IC1 | SHT25 | SHT25 | 1

TOP TE/MPE/EM Design Office

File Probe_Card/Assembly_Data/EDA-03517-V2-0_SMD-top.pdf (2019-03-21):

J1 | J4

# 1 SMD TOP

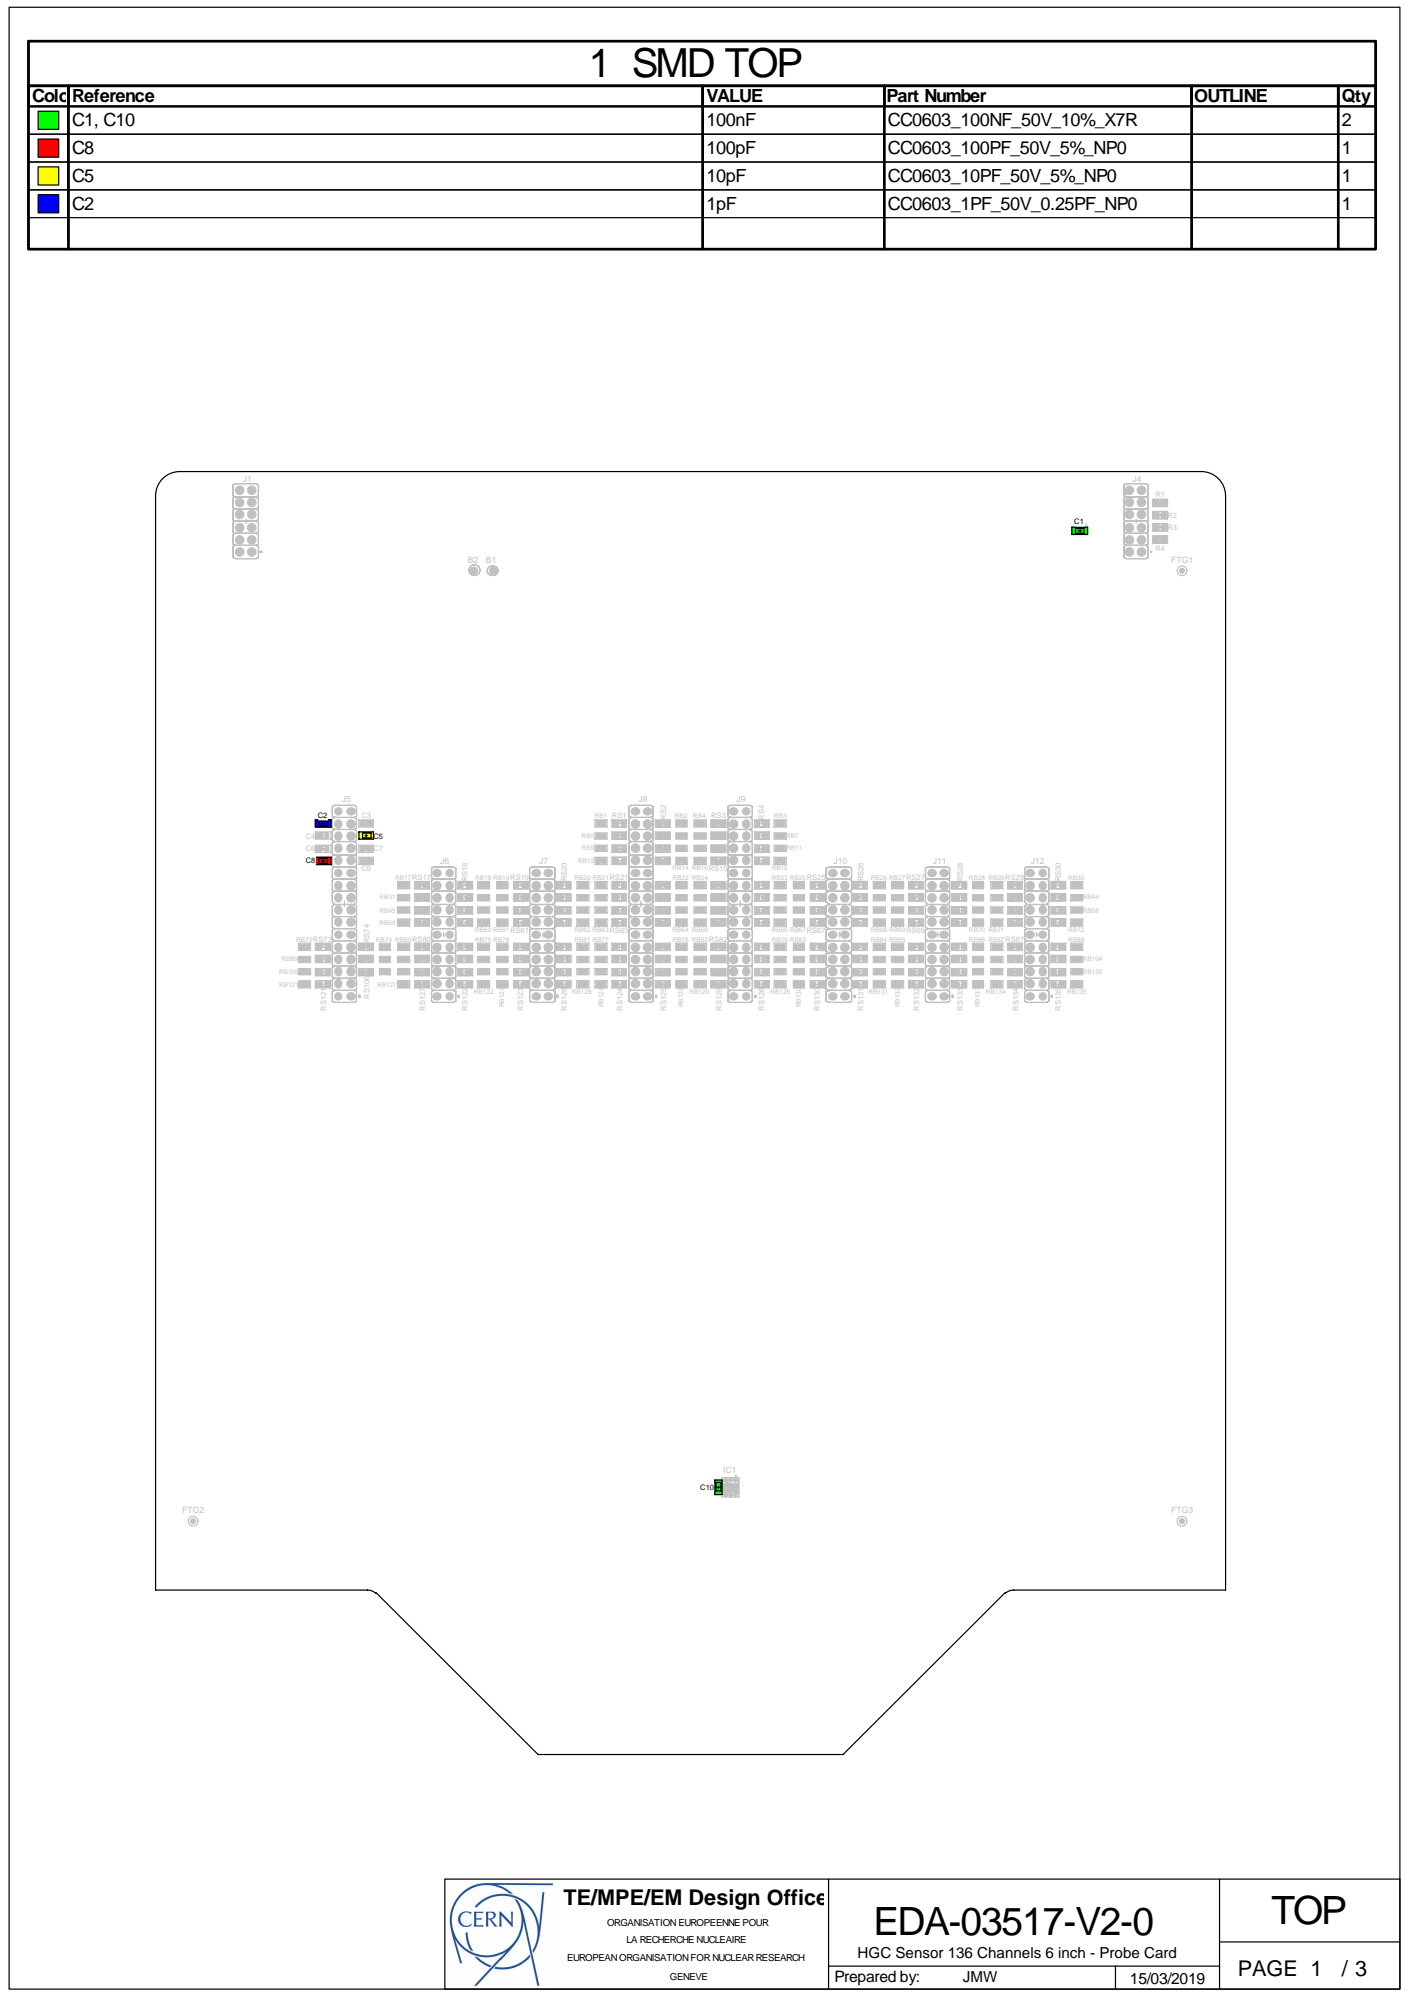
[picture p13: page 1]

TOP TE/MPE/EM Design Office

J1 | J4
C9 | 220pF | CC0603_220PF_50V_5%_NP0 | 1

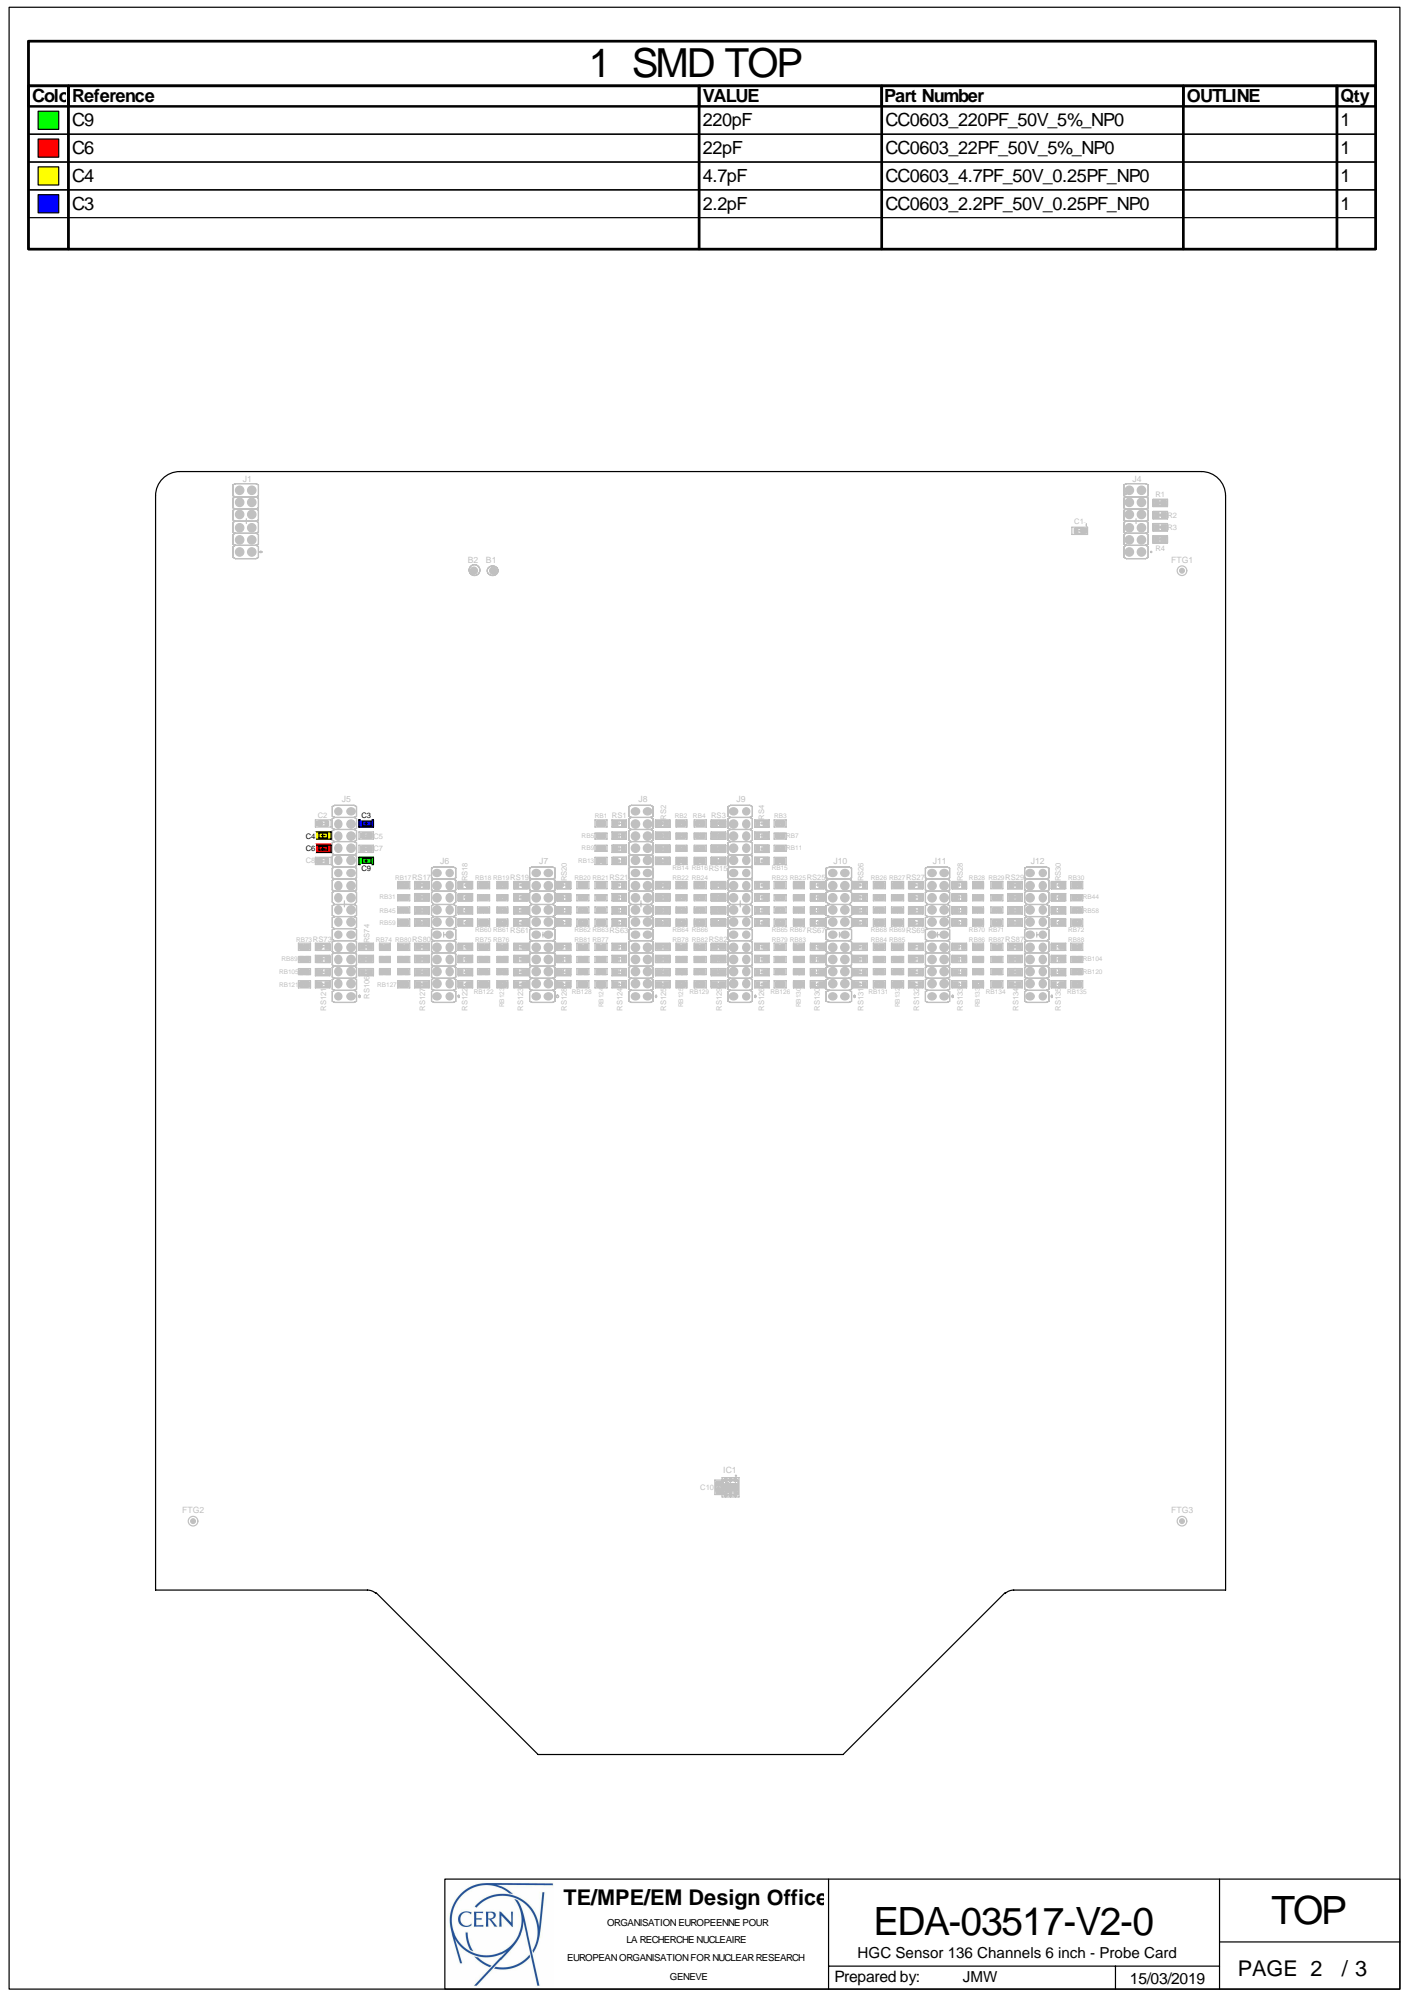
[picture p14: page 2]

J1 | J4
C7 | 47pF | CC0603_47PF_50V_5%_NP0 | 1

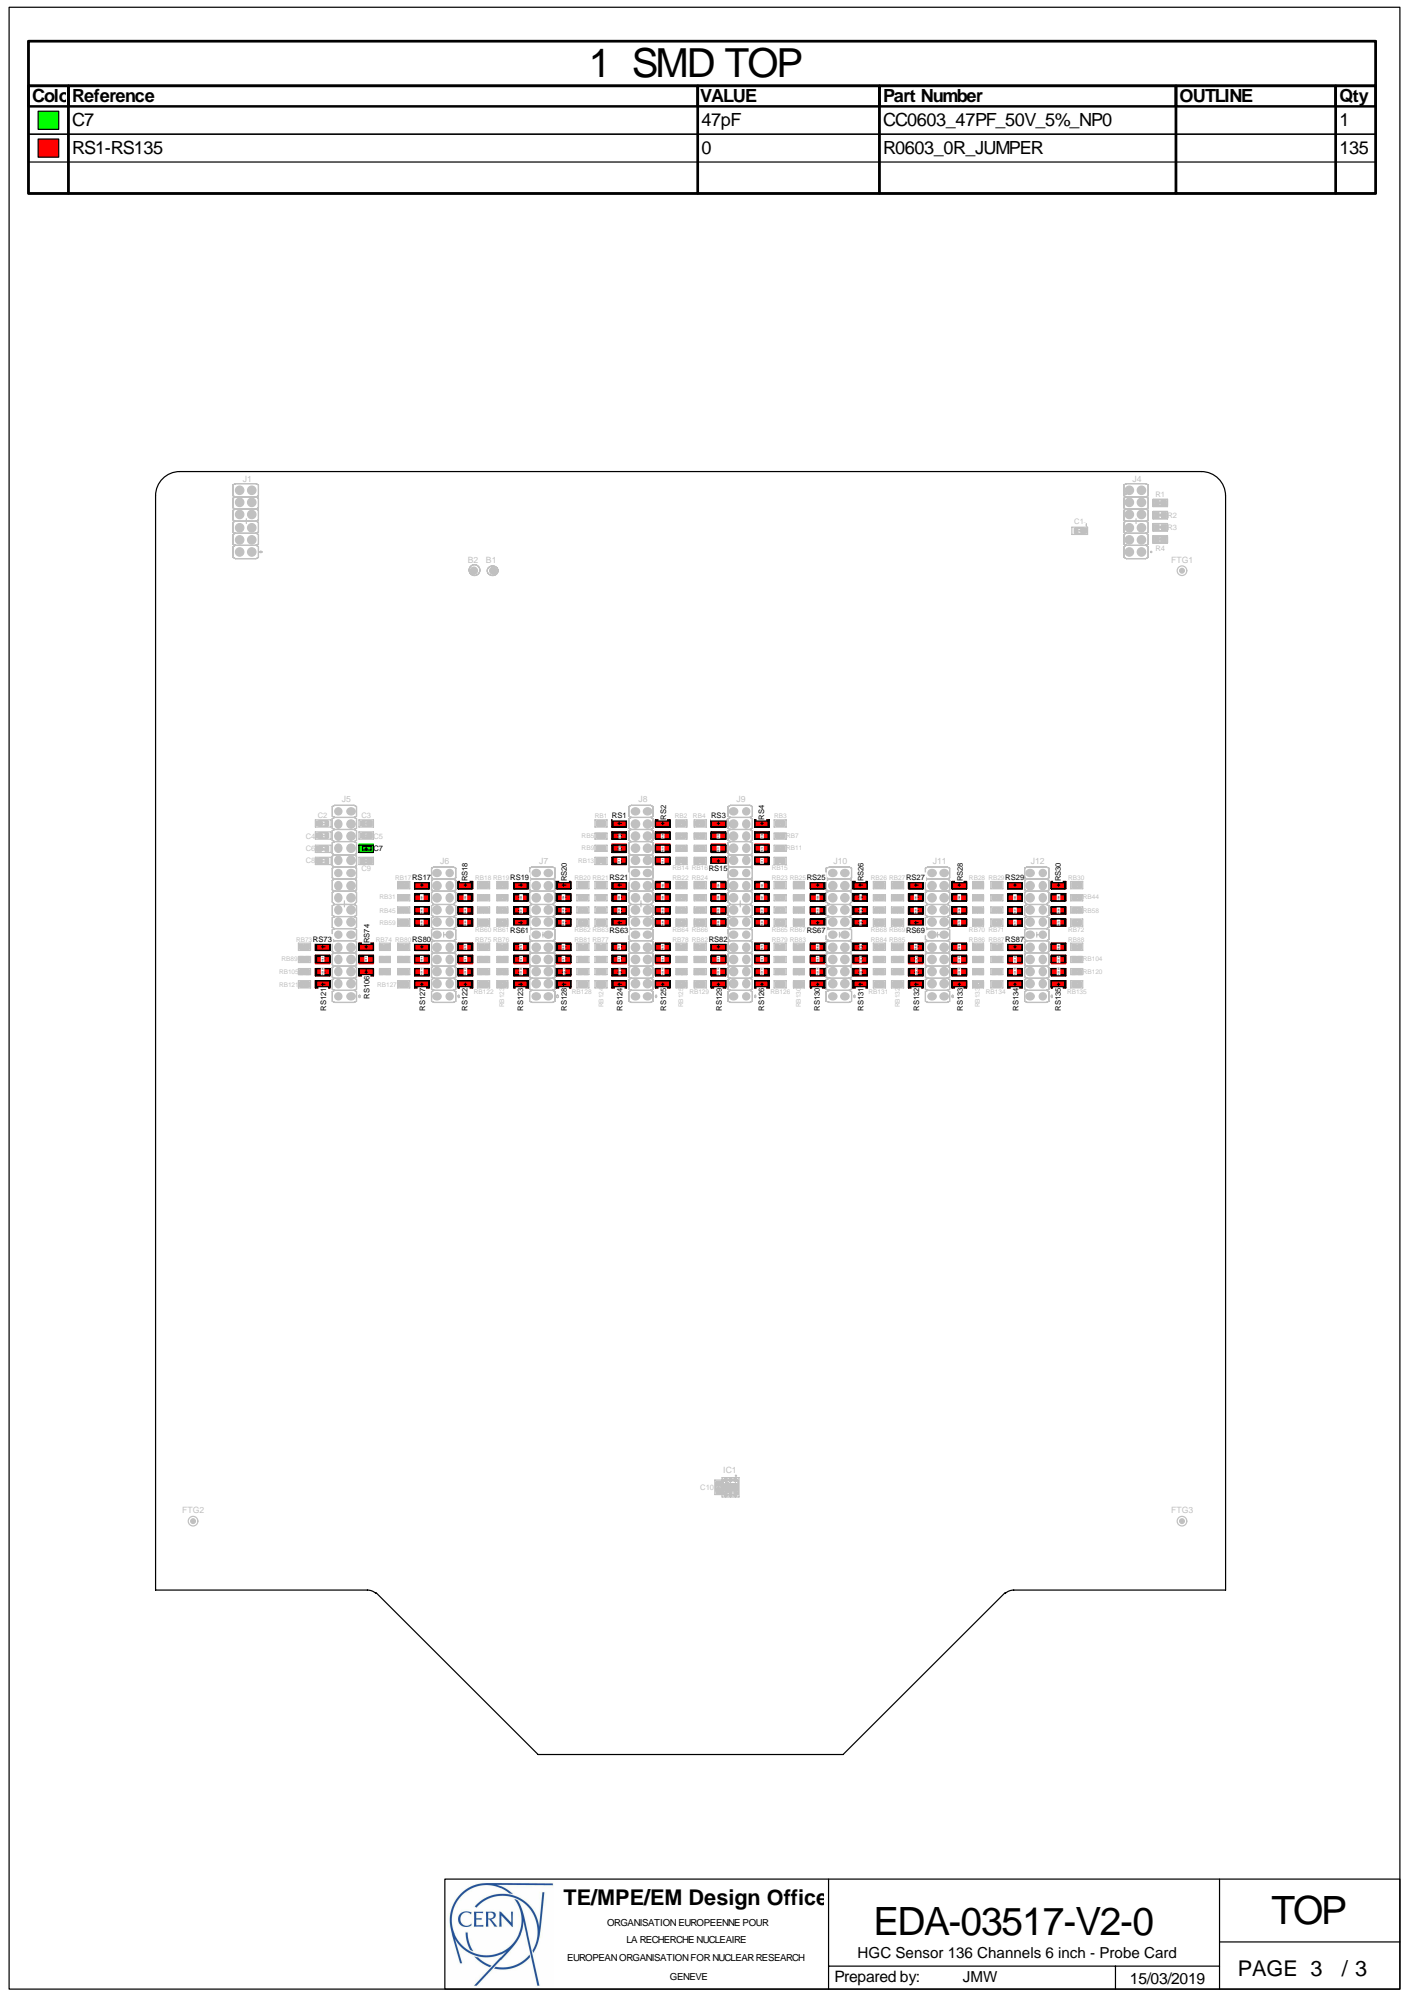
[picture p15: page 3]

RS1-RS135 | 0 | R0603_0R_JUMPER | 135

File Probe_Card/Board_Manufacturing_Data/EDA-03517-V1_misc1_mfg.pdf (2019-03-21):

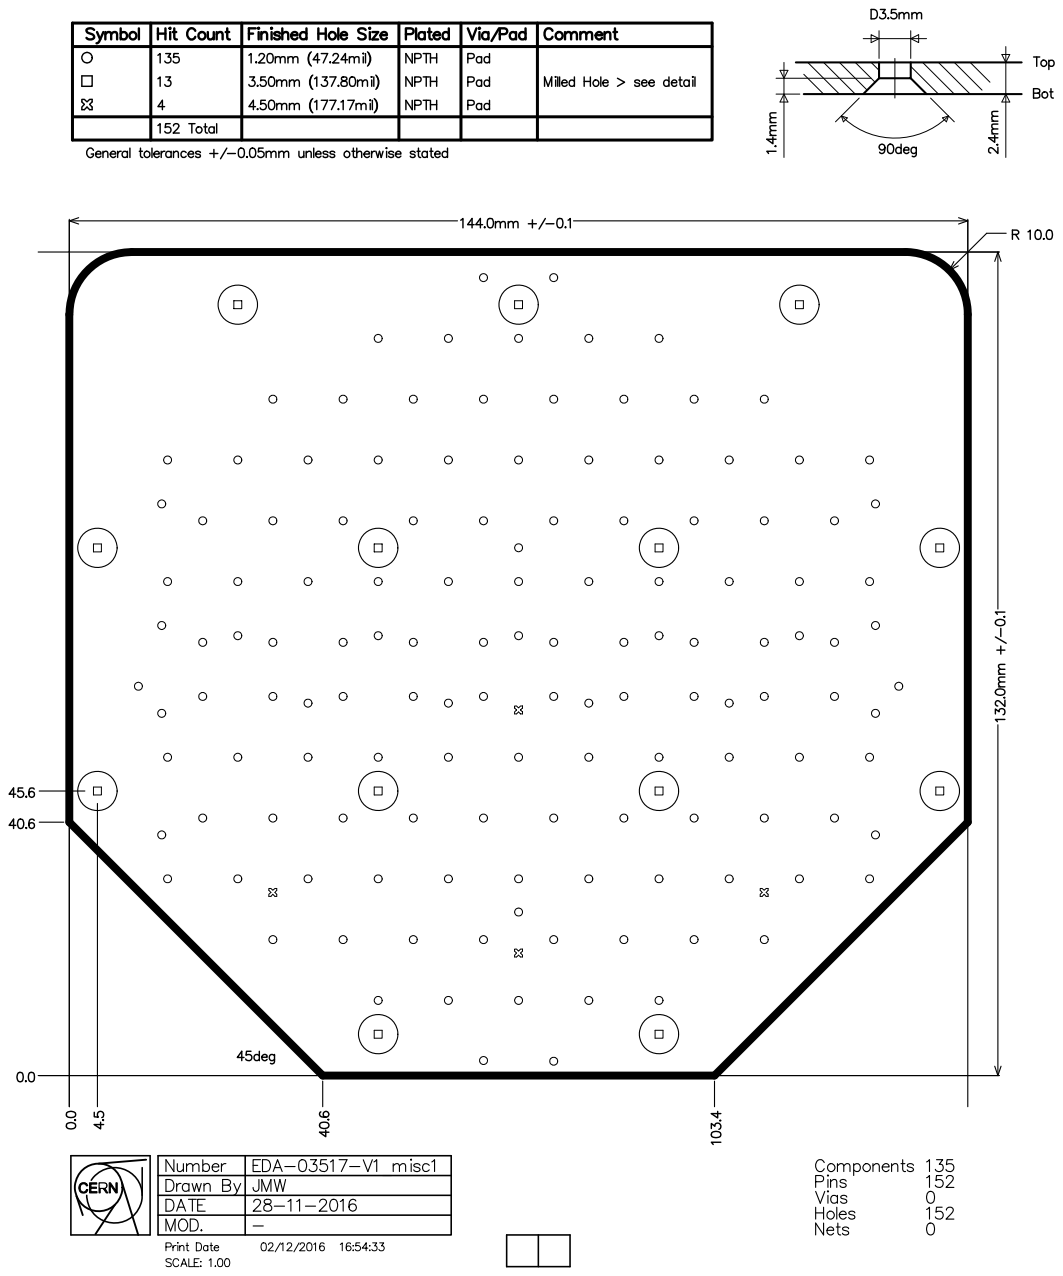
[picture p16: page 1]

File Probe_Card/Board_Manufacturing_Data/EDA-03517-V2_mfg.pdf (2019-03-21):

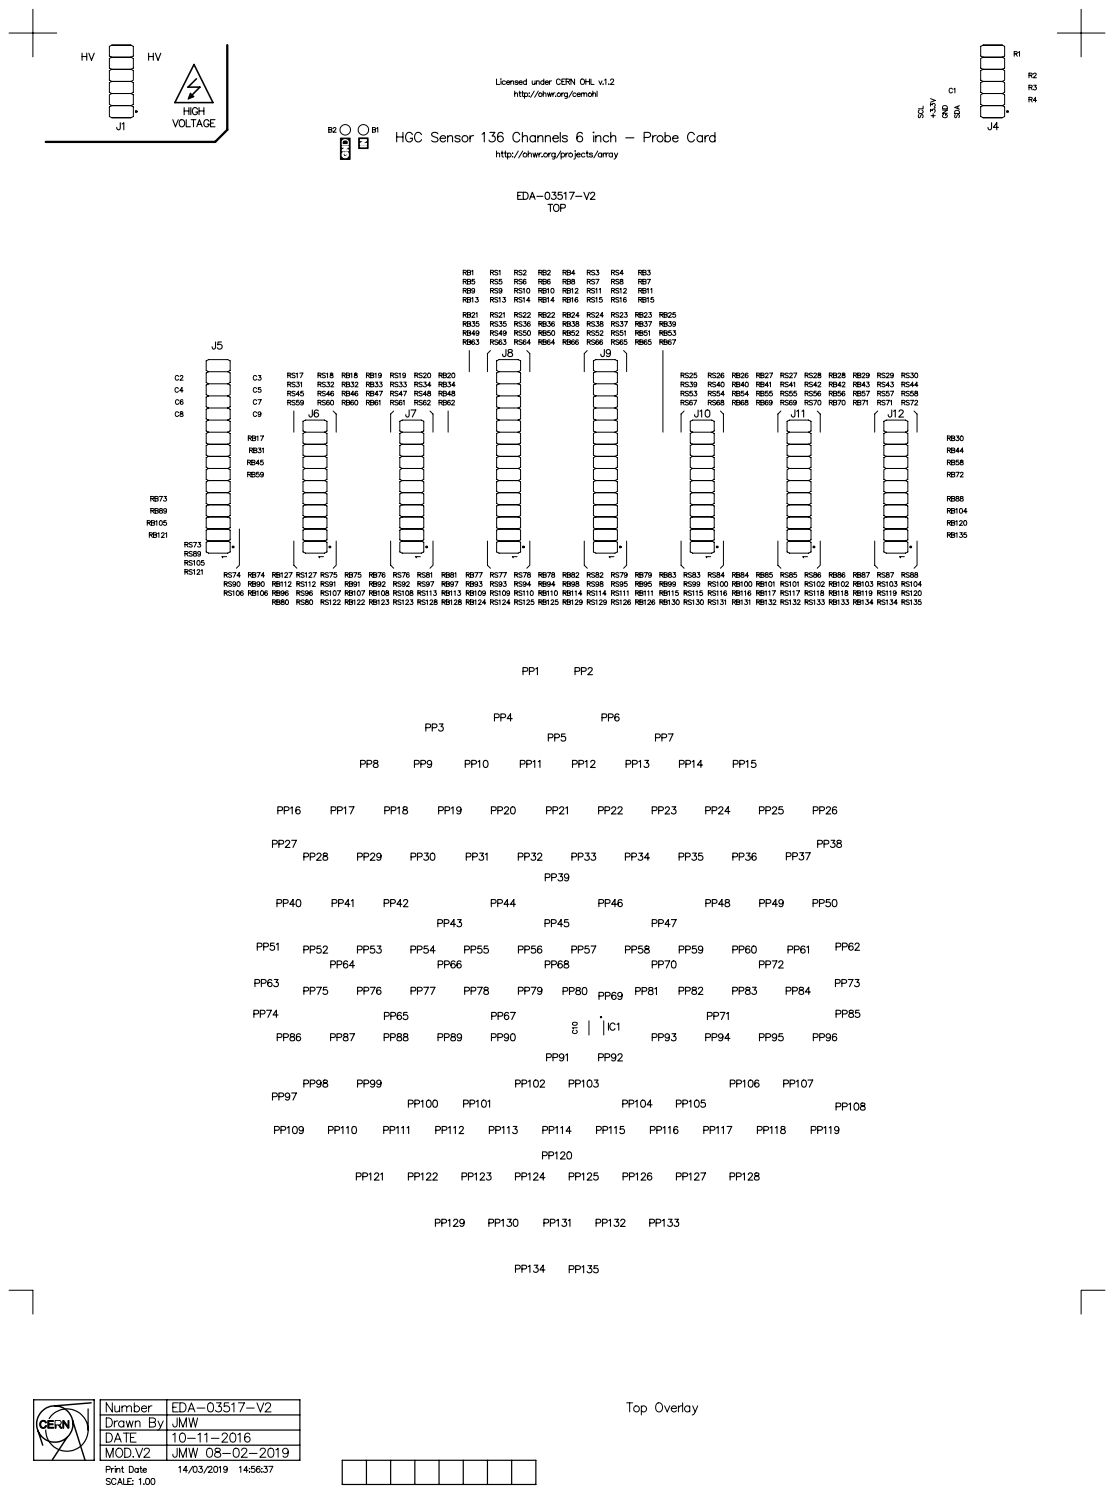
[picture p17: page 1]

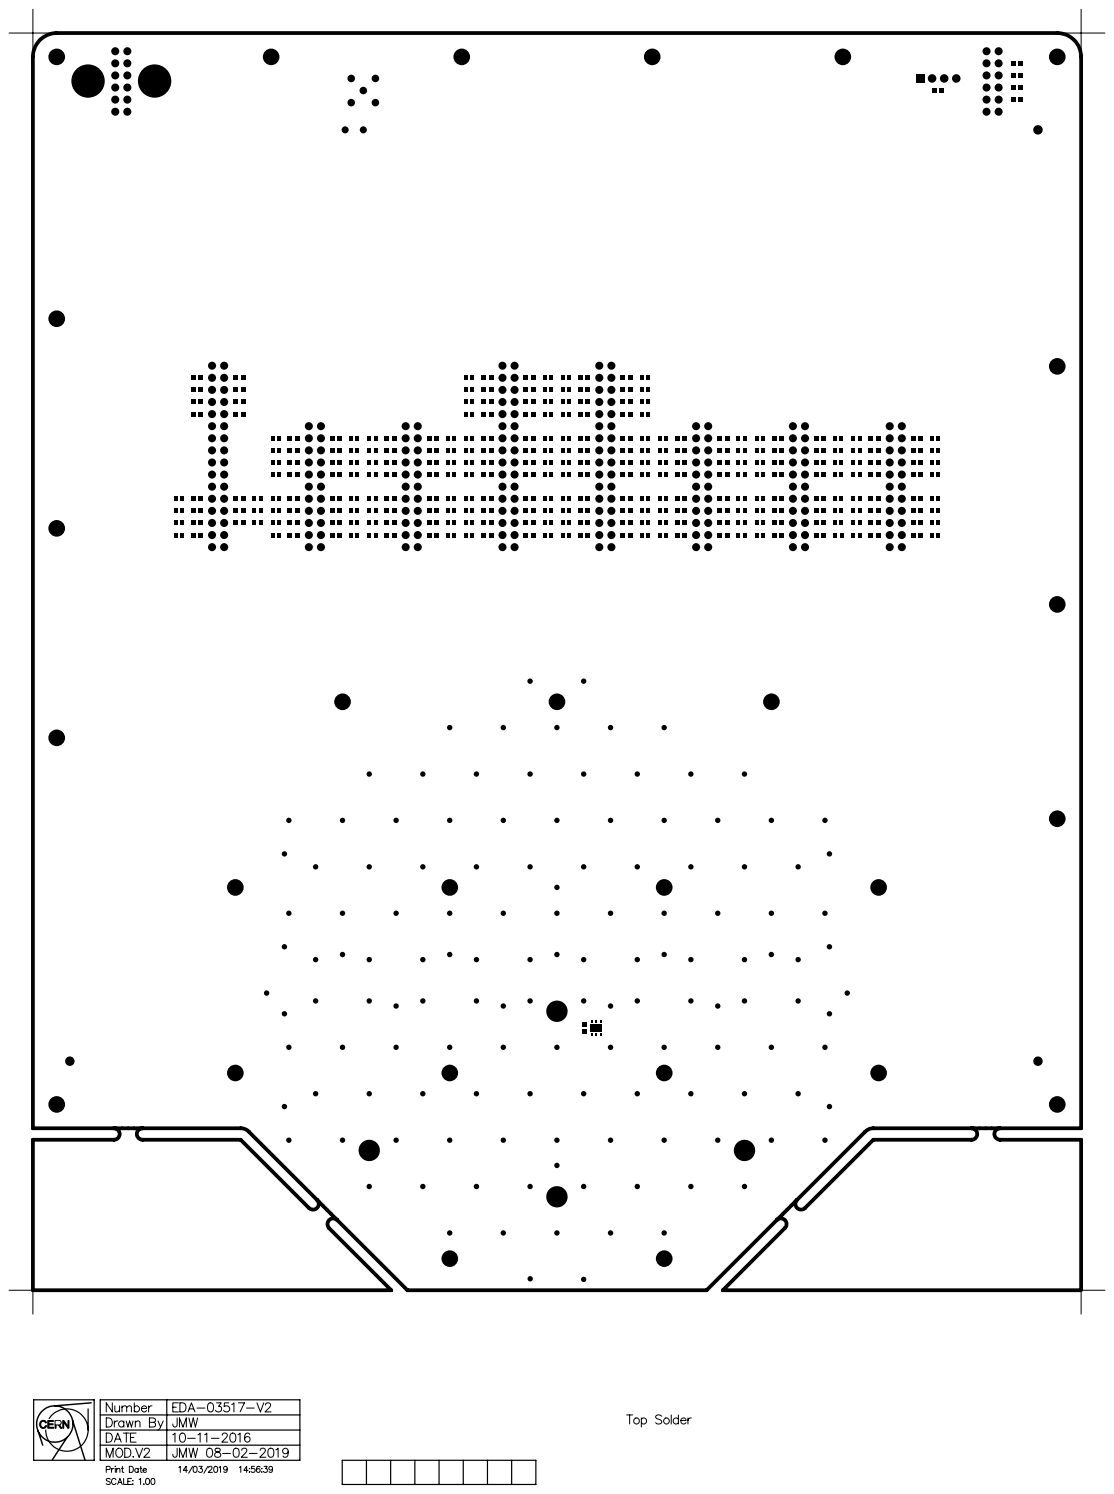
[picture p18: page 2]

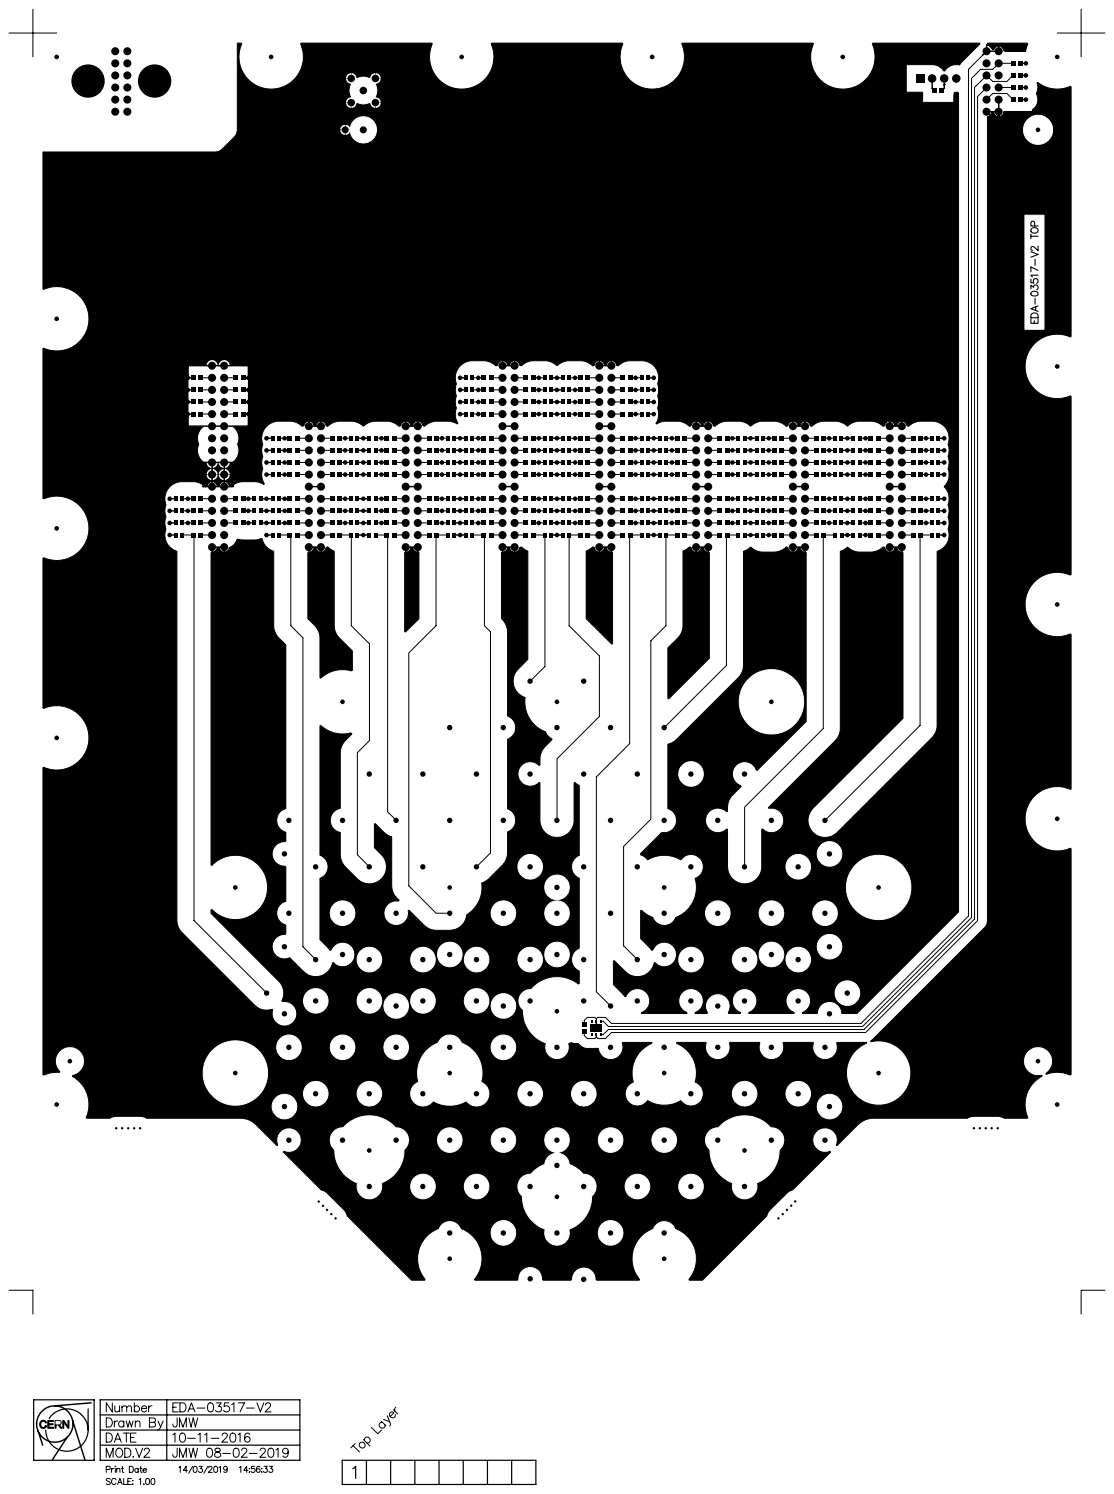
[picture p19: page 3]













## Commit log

2019-03-21 Added files of switching matrix
    [EDA-03518-V3-0_pcb-mat.xls]
2019-03-21 Added files of probe card
    [EDA-03517-V1-0_misc1.pcbdoc, EDA-03517-V2-0_arrangement-mat.xls, EDA-03517-V2-0_pcb-mat.xls]
